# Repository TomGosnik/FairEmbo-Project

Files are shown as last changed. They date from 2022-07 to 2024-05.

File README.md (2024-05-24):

# FairEmbo - Fragmentation of surgical suture thread: 0.3, 0.5, 0.7, 0.9 mm

  ## Context
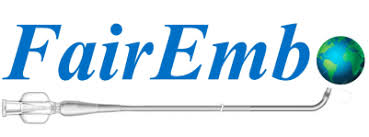
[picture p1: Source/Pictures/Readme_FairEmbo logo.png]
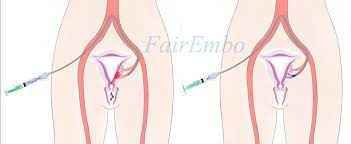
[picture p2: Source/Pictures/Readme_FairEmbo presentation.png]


This is part of a research project to previde a new solution to the problem of embolisation in low income countries. The [FAIREMBO chair](https://www.univ-amu.fr/en/public/fairembo-chair) from Marseille Hospital in France is a the origin of the innovation and we have here the plans of the machine that allows a mass cutting of particules necessary to achieve the operation.

Embolisation is a technology whose objective is to stop bleeding or blood circulation in a targeted area. The process seals a vessel by injecting a product into an artery under local anaesthetic. 

The embolisation procedure is not often used or considered in underdeveloped countries because embolisation equipment is simply not affordable in some countries. For one operation, several hundred euros are required, which is simply not possible in some cases. So there is an unaffordable demand for third world countries. In addition, the embolisation product is not well distributed in these countries, so additional costs would have to be incurred for importing the goods needed to carry out the procedure.
It is then necessary to find a solution to develop and provide embolisation procedures for underdeveloped countries. This solution must be affordable and easy to implement in these countries. 

In the search for an affordable solution to enable developing countries to access embolisation procedures, the Radiology and Medical Imaging Department of the Marseille Hospital (France) is proposing a new solution using suture particles injected in large quantities into the arteries to seal the vessels. 
In the case of the product used today, the embolisation is done chemically and increases the chance of thrombosis.
In the case of sutures, it is the mechanical effect of the accumulation of pieces of suture that allows the embolisation of the vessel. 

Our customer, contacted us to think about the creation of a machine to cut the suture before the medical intervention. The suture is given in spools and the prototype must provide the cut particles and answer different functions presented in the specifications of the machine.

The main objective of this project is to design and manufacture a device which is capable of taking input in the form of suture spools, and providing output in the form of cut sutures suitable for the FairEmbo process. The design should be simple, easy to use and, above all, cost-effective. In this way, the project will contribute to the automation of the Fairembo technique without losing sight of the main objective of affordability for poor underdeveloped countries.

This project has been initiated and developed in collaboration with the S-MART platform of Grenoble University (https://s-mart.grenoble-inp.fr/).

*For more information on the [FairEmbo project](https://www.youtube.com/watch?v=6P3fuX9SuC4)*

  ## Our product
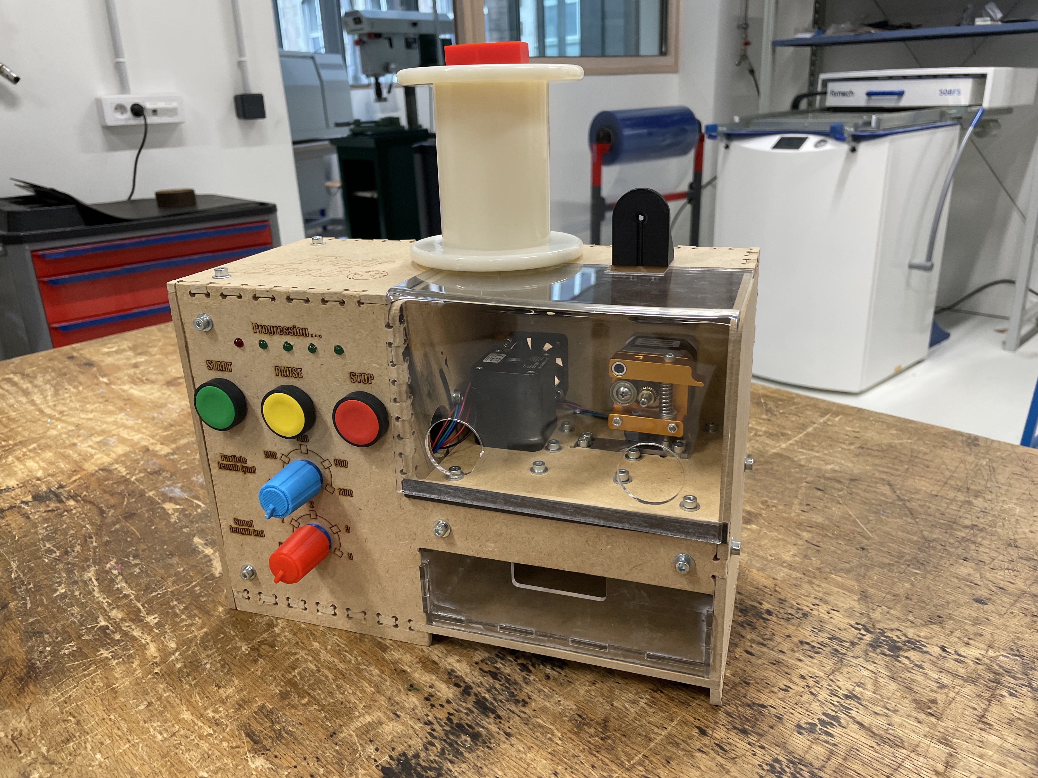
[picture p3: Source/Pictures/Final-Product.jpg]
  
  
  Photo of the particules as a result of the cutting operation: 0.3, 0.5, 0.7, 0.9 mm
    
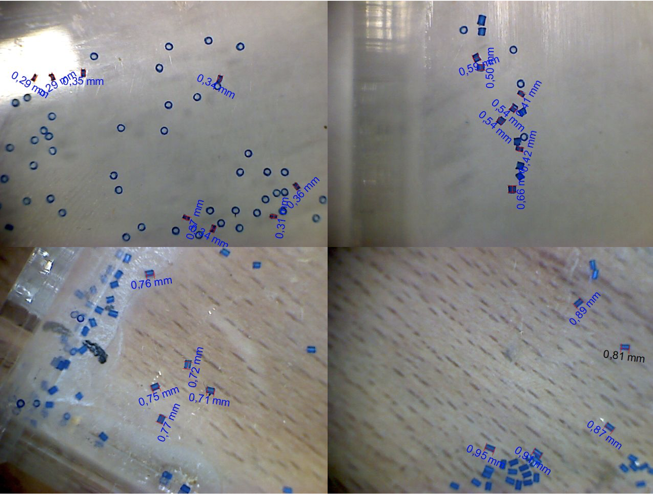
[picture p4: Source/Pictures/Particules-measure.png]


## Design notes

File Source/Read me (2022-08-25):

Insert Here a presentation of the content of the repository

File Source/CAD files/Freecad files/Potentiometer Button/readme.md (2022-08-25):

This component is downloaded from tracepart
# link of this component:
[Bouton de potentiomètre Sifam, axe de 6mm, Diamètre de 11mm, Enfichable](https://www.traceparts.com/fr/product/rs-components-bouton-de-potentiometre-sifam-axe-de-6mm-diametre-de-11mm-enfichable?CatalogPath=TRACEPARTS%3ATP10015001008002002&Product=10-23022015-110121&PartNumber=3%2F03%2FDR110-006%2F237%2F224)

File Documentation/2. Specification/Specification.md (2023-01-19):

# Specification
  
## 1. Stakeholders:
  
**Definition:** *Stakeholders generally refer to all the actors (human and non-human) who have an interest in a product. Among the stakeholders, there are both internal players, such as users and participants of the project, and external players that are represented by the potential user of products or external entities.*

<p align="center">
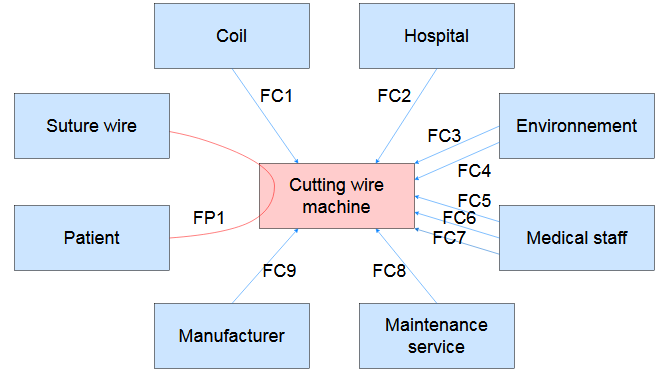
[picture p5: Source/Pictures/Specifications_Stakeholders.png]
  
<p/>

**FP1:** Cutting suture into particles

**FC1:** Be able to adapt to several types of suture bobbins

**FC2:** Be inexpensive

**FC3:** Be robust

**FC4:** Be able to adapt to its environment

**FC5:** Be lightweight and small in size

**FC6:** Be self-contained

**FC7:** Be easy to use

**FC8:** Be maintainable

**FC9:** Be reproducible
  
## 2. External interfaces
  
**Definition:**  *External interfaces are interactions between the product and the stakeholders.*

<p align="center">
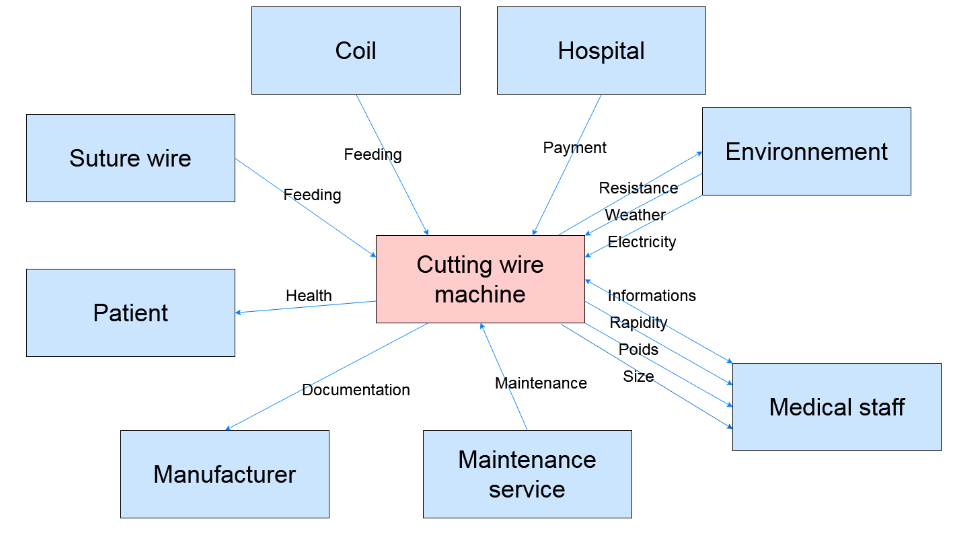
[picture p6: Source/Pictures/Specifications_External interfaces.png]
  
<p/>

## 3. Requirement

**Definition:** *A requirement is a formal statement that specifies when condition C is true, property P of object O is actual and its value shall belong  to domain D.*

* Cutting suture into particles
  * Particle size : between 300 and 1100 µm	(precision +/-75µm)
  * thread diameter : 0.3 to 0.5 extruded surgical suture thread
  * Particle shape : cylindrical (validated if the particles can exit the syringe)
  * Particle recovery
  * Speed of the process : less than 1s/particle

* Be able to adapt to several types of suture bobbins
  * Inner diameter 
  * Outside diameter
  * Wire length

* Be inexpensive
  * Cost : less than 500€ in parts

* Be robust
  * Drop resistance : functional after a drop of at least 1m
  * Lifetime 

* Be self-contained
  * Unattended operation time : Stops only when there is no more wire or when the user requests it (+/- 1s)

* Be easy to use
  * User documentation : can be used without instructions or training (possibility to integrate operating steps)
  * Accessibility of controls : can be used without the need for special dexterity
  * Quick to set up : less than 5 minutes

* Be maintainable
  * Demountability : access to components in the machine possible by hand or with a simple tool
  * Accessible materials, manufacturing techniques and components : use of materials, manufacturing techniques and components found in a conventional FabLab

* Be reproducible
  * Comprehensive documentation content : must be comprehensive and clear enough to be constructed by a third party
  * Accessibility of documentation : must be found on the internet
  * Accessible materials, manufacturing techniques and components : use of materials, manufacturing techniques and components found in a conventional FabLab

* Be lightweight and small in size
  * Mass : less than 3kg
  * Volume : between 3 and 10 dm3
 
* Be able to adapt to its environment
  * Power supply : 230V (+/- 1V)
  * Temperature : between 0 and 50 °C

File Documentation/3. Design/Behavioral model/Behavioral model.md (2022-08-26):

# Behavioral model

The system is composed of two mechanically moving parts. These two movements are driven by the two stepper motors: 
- the one linked to the extruder which guides and advances the wire,
- the one linked to the cam which cuts the wire.

## Wire guide

The first stepper motor is connected to an extruder, used today in 3D printers. An extruder is composed of different parts that are important for its operation:
- a gear wheel attached to the motor shaft,
- a ball bearing pressed against the gear wheel to prevent the wire from slipping,
- a nozzle that guides the wire to the place where it will be cut.

The gear wheel drives the bearing, which causes the wire to translate as shown below.
The translation and therefore the step corresponding to the size of the cut particles are therefore the image of the step imposed by the stepper motor.

<p align="center"> 
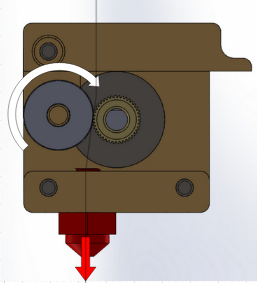
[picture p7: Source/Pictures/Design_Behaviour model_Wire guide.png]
 
</p>

## Wire cutting

The principle of cutting is that of the cam which transforms the rotational movement imposed by the motor into a translational movement.
A cam is an off-axis cylinder, i.e. the radius is not the same depending on the angle of rotation. It is this difference in radius that allows the red part to be translated (see below). 

To avoid friction, a ball bearing is used to link the cam and the red part.

This red part is guided in translation with a rail system. This red part is also directly screwed to the mobile blade, which is itself in translation against the second immobile blade.

In order to be able to move back and forth on the blade system, it was decided to use springs so that the red part could return to its initial position.

<p align="center"> 
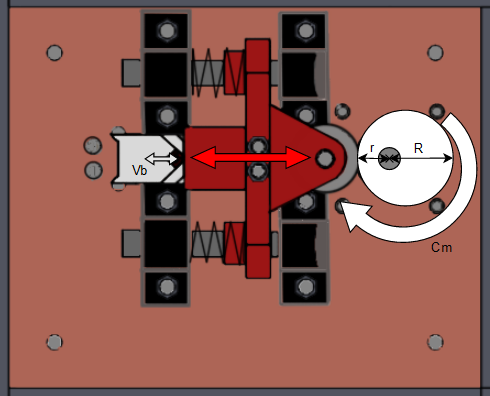
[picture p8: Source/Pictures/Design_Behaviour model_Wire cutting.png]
 
</p>

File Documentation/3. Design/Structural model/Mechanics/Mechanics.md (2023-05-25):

# How to document a structural model of mechanical products? 

 ## 1. Architectural structure

- **Definition:** *The architectural structure is a physical or logical layout of the components of a system design and their internal and external connections.*

 ### Architectural tree
 
<p align="center">
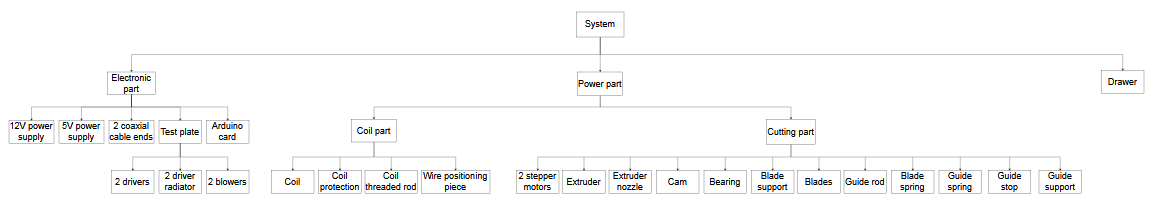
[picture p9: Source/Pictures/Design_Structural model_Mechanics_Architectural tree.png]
  
</p>
 
   ### Architectural graph

 - **Explanation:** The Template contains 2 main flow streams : 1. Power supply(represented in red), 2. Suture Wire (represented in green)

<p align="center">
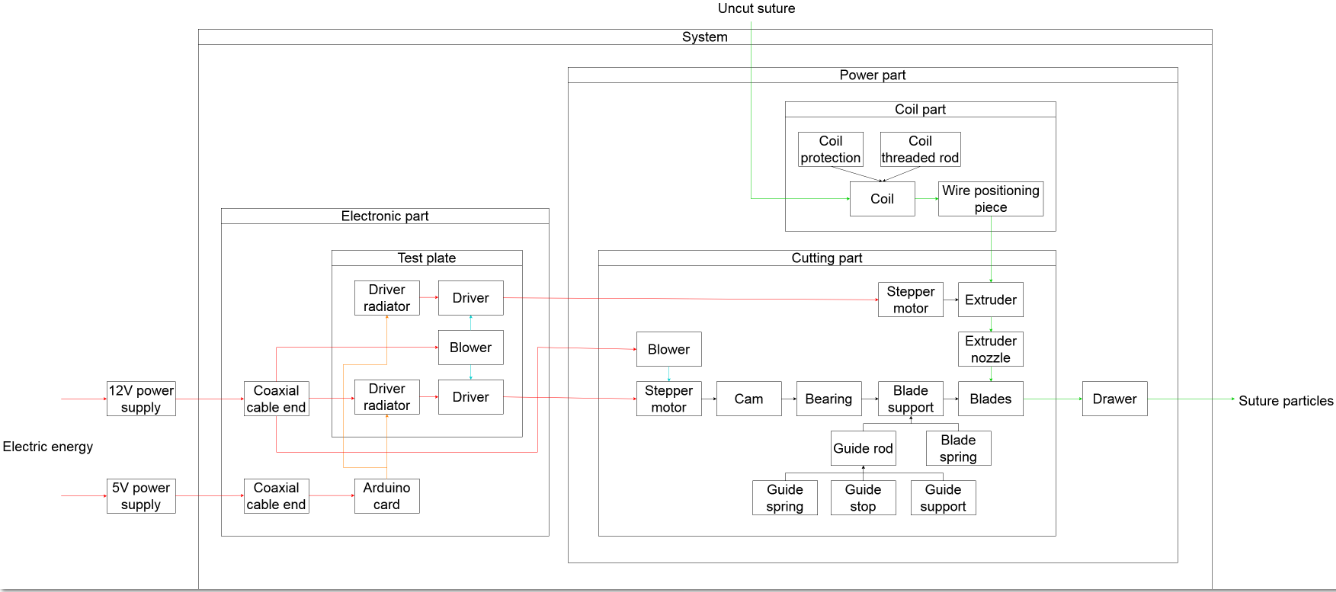
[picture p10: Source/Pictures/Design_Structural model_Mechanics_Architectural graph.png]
  
</p>

## 2. Editable CAD files
 *Fairembo was designed in SolidWorks (version 2021) and Freecad (version 0.19), allowing you to have full access to view, copy, edit, and export all of the source 3D CAD models for free from any computer which has installed Freecad and SolidWorks* 

  ### Template of file format

  1. 3D/2D file format
     * '.FCStd' is the original Freecad file format, allowing you to change the dimensions of the component as you want
     * '.STEP' is a neutral format which is for representative use such as Stepper Motor, Arduino card.
     * '.Dxf' is a 2D file format which allow you to use it in laser cutting
     * '.Stl' is a 3D file format which mostly used in 3D printing
  2. Name of CAD software

 Name of software | Version used | Download link 
|:---:|:---:|:---:|
SolidWorks | 2021 | https://www.solidworks.com/sw/support/downloads.htm 
FreeCAD| 0.19 | https://www.freecadweb.org/downloads.php
OnShape | 2021 |https://cad.onshape.com/documents/1c97d2eae284a43686a399bf/w/0fb098345c6d2285c3f1eb61/e/92be17f8a49da64bbd5fd24f
 
## 3. Characteristics of the materials
  
   ### Table of material Characteristics
 
 Name of material |	Density (g/cm3) |	Compressive Strength (MPa) |	Elastic Modulus (GPa) | Max Operating Temp (°C) | life span (years) | Price(european region) |	 Advantage |  Disadvantage |	link of reference 
|:---:|:---:|:---:|:---:|:---:|:---:|:---:|:---:|:---:|:---:|
Medium density fibreboard(MDF) | 0.75 | 10 | 4.0 | up to 130 | more than 10 | 7€ per m2 for thickness of 3mm | inexpensive, easy to recycle, solid, easy to manufacture (laser cutting, paint...) | heavy, absorb water faster than wood | [Medium Density Fiberboard](https://www.makeitfrom.com/material-properties/Medium-Density-Fiberboard-MDF/), [Physical and mechanical properties of MDF panels containing burned wood](https://www.researchgate.net/figure/Physical-and-mechanical-properties-of-MDF-panels-containing-burned-wood_tbl3_257485673), [Maximum core temperature (MCT) for MDF mats at various MCs](https://www.researchgate.net/figure/Maximum-core-temperature-MCT-for-MDF-mats-at-various-MCs_fig4_237372503), [Advantages & Disadvantages of MDF - Fiber Board](https://civiltoday.com/civil-engineering-materials/timber/163-advantages-and-disadvantages-of-mdf), [Price for MDF in France](https://www.smbois.com/panneaux-bois/panneaux-mdf/mdf.html)
Plexiglass (PMMA) | 1.18 | 75,84 to 131 | - | 65 to 93 | 30 and even more | 25€ to 140€ per m2 for thickness from 1mm to 15mm | inexpensive, easy to manufacture (laser cutting, folding...), light | not resistant to heat | [Technical Data Sheet Plexiglass (PMMA)](https://laminatedplastics.com/plexiglass.pdf), [PLEXIGLAS®: A VALUABLE MATERIAL EVEN AFTER USE](https://www.plexiglas.de/en/sustainability/easy-to-recycle), [Acrylic advantages and disadvantages](https://plasticsheetsshop.co.uk/acrylic-advantages-and-disadvantages/#:~:text=Advantage%3A%20Plexiglass%20is%20hardwearing%20Acrylic%20sheet%20is%20very,same%20levels%20of%20thermal%20efficiency%20as%20standard%20glass), [plexiglas shop](https://www.plexiglas-shop.com/)
Aluminum | 2.6898 | - | 68.3 | - | 40 to 80 | 2.1€ to 3.5€ per Kg | lighter than other metal, easy to manufacture( lathe, milling..) | - | [Aluminium: Specifications, Properties, Classifications and Classes](https://www.azom.com/article.aspx?ArticleID=2863), [THE LIFESPAN AND RECYCLABILITY OF ALUMINIUM AND STAINLESS STEEL](https://www.metalswarehouse.co.uk/lifespan-recyclability-aluminium-steel/), [Aluminium Price Today](https://markets.businessinsider.com/commodities/aluminum-price/euro#:~:text=1%20Ton%20%3D%201%2C000%20Kilograms.%20%0AAluminium%20Price%20,%20%20%20Per%201%20Kilogram.%202.34%20EUR).
Acrylonitrile butadiene styrene (ABS) | 0.9 to 1.53 | 65 | 2.28 | −20 to 80 | 50 to 80 | 25$ per Kg | resistant to physical impact, easy to use for 3D print | inappropriate for high-temperature condition, high smoke generation when it burns| [ABS's properties from wiki](https://en.wikipedia.org/wiki/Acrylonitrile_butadiene_styrene), [Typical Compressive Yield Strength and Compressive Modulus of Polymers](https://matweb.com/reference/compressivestrength.aspx), [What is the average life expectancy of ABS pipe?](https://www.howtolookatahouse.com/Blog/Entries/2018/7/what-is-the-average-life-expectancy-of-abs-pipe-1.html#:~:text=The%20expected%20lifespan%20of%20ABS%20%28Acrylonitrile%20Butadiene%20Styrene%29,is%20expected%20to%20be%20similar%20to%20PVC%20pipe), [ABS plastic properties](https://adrecoplastics.co.uk/abs-plastic-properties/#:~:text=ABS%20has%20a%20low%20melting%20point%2C%20which%20enables,to%20withstand%20heavy%20use%20and%20adverse%20environmental%20conditions), [How Much Does 3D Printing Filament Cost](https://3dinsider.com/3d-printing-filament-cost/#:~:text=Regular%20PLA%20and%20ABS%20filament%20for%203D%20printing,amount.%20Not%20all%203D%20printing%20materials%20are%20equal).

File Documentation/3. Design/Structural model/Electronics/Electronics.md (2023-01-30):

# Structural model: Electronics

## 1. Nomenclature

The list of components with references and examples of links to usable sites:

Component name	| Nomenclature |	number of components |	Characteristics |	Links to the sites |	Unit price (€)|
| :---: | :---: | :---: | :---: | :---: | :---: |
Stepper motor 1 (M1) |	PUISS_Mot_Extr |	1	| Moteur pas à pas Joy-it SM42HT38-1684A NEMA-17-01 0.4 Nm 1.68 A Diamètre de l'arbre: 5 mm 1 pc(s) |	https://www.conrad.fr/p/moteur-pas-a-pas-joy-it-nema-17-01-04-nm-168-a-diametre-de-larbre-5-mm-1-pcs-1597325	| 31,99 |
Stepper motor 2 (M2) |	PUISS_Mot_Cam |	1	| Joy-it Moteur pas à pas NEMA17-06 0.59 Nm 2 A 2 A Diamètre de l'arbre: 5 mm |	https://www.conrad.fr/p/joy-it-moteur-pas-a-pas-nema17-06-059-nm-2-a-2-a-diametre-de-larbre-5-mm-2355876	| 21,49 |
Driver 1 (D1)	| ELEC_Driv_Extr |	2	| TB6612FNG Dual Motor Driver Carrier	| https://www.pololu.com/product/713	| 9,95 |  
Driver 2 (D2)	| ELEC_Driv_Cam	|
Driver 1 radiator	| ELEC_Rad_Driv_Extr	| 2	 | Résistance thermique:123°C/W; Boîtiers refroidis:SOIC-8, SOIC-14, SSOP-16, TSSOP-14, TSSOP-16; Largeur externe - Métrique:6.3mm; Hauteur externe - Métrique:4.8mm; Longueur externe - 	| https://fr.farnell.com/webapp/wcs/stores/servlet /CompareProductsDisplay?catalogId=15001&langId=-2&storeId=10160&catentryId=64708491&pageType=PDP	| 0,618 | 
Driver 2 radiator	| ELEC_Rad_Driv_Cam | 				
Capacitor (C)	| ELEC_Cond	| 1	| Capacitor 47μF, 16V c.c.	| https://fr.rs-online.com/web/p/condensateurs-electrolytiques/7110927?cm_mmc=FR-PLA-DS3A-_-google-_-CSS_FR_FR_Passifs_Whoop-_-(FR:Whoop!)+Condensateurs+%C3%A9lectrolytiques-_-7110927&matchtype=&pla-339621668050&gclid=Cj0KCQjwxIOXBhCrARIsAL1QFCaT7Q_rE7X_4SQt8N8Zu6aHp6PKWwv3yTqLVZFDtoSgLZNFndHlv44aApaUEALw_wcB&gclsrc=aw.ds	| 0,078 | 
Pushbutton 1 (B1)	| ELEC_Bout_V	| 3	| Bouton-poussoir, NO, Montage panneau	| https://fr.rs-online.com/web/p/boutons-poussoirs/8151834?aud-871567053779%3Apla-365975203081&cm_mmc=FR-PLA-DS3A-_-google-_-CFS_FR_FR_Schneider_Whoop-_-(FR%3AWhoop!)%20Interrupteurs%20(2)-_-8151834&gclid=Cj0KCQjwxIOXBhCrARIsAL1QFCZbOdo6Ri0mEeT1leJcbMdhEjlsmj2F4bzqcQj8dS_wv5ovp86AldUaAt9hEALw_wcB&gclsrc=aw.ds&matchtype=	| 16,9 | 
Pushbutton 2 (B2)	| ELEC_Bout_J	|  
Pushbutton 3 (B3)	| ELEC_Bout_R	|  
Potentiometer 1 (P1)	| ELEC_Pot_H	| 2	| Potentiometer: Resistance 10kohm, 1 turn, Linear, 500mW, resistance tolerance ± 20%	| https://fr.farnell.com/tt-electronics-bi-technologies/p231-fc20br10k/potentiometre-rotatif-10k-20mm/dp/2771755?st=potentiometre%20rotatif	| 1,68 | 
Potentiometer 2 (P2)	| ELEC_Pot_B	| 			
Green LED 1 (L1)	| ELEC_LED_1	| 4	| LED Vert, Traversant, 5 mm (T-1 3/4), 2 V	| https://fr.rs-online.com/web/p/leds/7088022p?cm_mmc=FR-PLA-DS3A-_-google-_-CSS_FR_FR_Afficheurs_et_optoelectronique_Whoop-_-(FR:Whoop!)+LEDs-_-7088022P&matchtype=&pla-834413916684&gclid=Cj0KCQjwxIOXBhCrARIsAL1QFCYk1e3LMUt7p1XBNJRN2BUuUm2WMwk3iOHTFCnizzsr4hlkoqhmzT8aAi9eEALw_wcB&gclsrc=aw.ds	| 0,268 | 
Green LED 2 (L2)	| ELEC_LED_2	| 	
Green LED 3 (L3)	| ELEC_LED_3	| 		
Green LED 4 (L4)	| ELEC_LED_4	| 			
Red LED 5 (L5)	| ELEC_LED_5	| 1	| LED Rouge, Traversant, 5 mm (T-1 3/4), 2,6 V	| https://fr.rs-online.com/web/p/leds/1278393?cm_mmc=FR-PLA-DS3A-_-google-_-CSS_FR_FR_Afficheurs_et_optoelectronique_Whoop-_-(FR:Whoop!)+LEDs-_-1278393&matchtype=&pla-302722872933&gclid=Cj0KCQjwxIOXBhCrARIsAL1QFCYVfGLEzypoiNEvZWrra4NUpec1AlHI-cAAueNsmEW-s_PTFDmVd0UaAoqTEALw_wcB&gclsrc=aw.ds	| 0,088 | 
Resistance 1 (R1)	| ELEC_Resist_Bout_V	| 8	| Résistance Film carbone 100Ω ±5%, 0.25W	| https://fr.rs-online.com/web/p/resistances-traversantes/7077587	| 0,278 | 
Resistance 2 (R2)	| ELEC_Resist_Bout_J | 		
Resistance 3 (R3)	| ELEC_Resist_Bout_R | 			
Resistance 4 (R4)	| ELEC_Resist_LED_1	| 		
Resistance 5 (R5)	| ELEC_Resist_LED_2	| 			
Resistance 6 (R6)	| ELEC_Resist_LED_3	| 		
Resistance 7 (R7)	| ELEC_Resist_LED_4	| 			
Resistance 8 (R8)	| ELEC_Resist_LED_5	| 
5V power supply	| ELEC_Alim5V	| 1	| Alimentation AC/DC, ITE, 1 sortie, 2.75 W, 5 V, 550 mA	| https://fr.farnell.com/brainboxes/pw-600/power-supply-5v-1a-es-357/dp/2096366?st=alimentation%205v	| 27,77 | 
12V power supply	| ELEC_Alim12V	| 1	| Adaptateur AC/DC 12V c.c., 2A, 24W, , Régulée	| https://fr.rs-online.com/web/p/adaptateurs-ac-dc/1753324?cm_mmc=FR-PLA-DS3A-_-google-_-CSS_FR_FR_Alimentations_et_transformateurs_Whoop-_-(FR:Whoop!)+Adaptateurs+AC/DC-_-1753324&matchtype=&pla-370976687757&gclid=Cj0KCQjwxIOXBhCrARIsAL1QFCbjgBdOY3BMhupPiywYVdsT5aeT05L4zefR6RXDtFUW6gS1CuGbczEaAmj8EALw_wcB&gclsrc=aw.ds	| 16,26 | 
5V coaxial cable end	| ELEC_Embout_5V	| 2	| Prise d'alimentation CC, 5A, Montage sur CI, 12 V c.c.	| https://fr.rs-online.com/web/p/connecteurs-d-alimentation-dc/8051696	| 2,359 | 
12V coaxial cable end	| ELEC_Embout_12V	| 		
Ventilator 1	| ELEC_Ventilo_Mot	| 2	| Ventilateur axial RS PRO 5 V c.c., 11.9m³/h, 40 x 40 x 10mm, 1.92W	| https://fr.rs-online.com/web/p/ventilateurs-axiaux/7897858?cm_mmc=FR-PLA-DS3A-_-google-_-CSS_FR_FR_Chauffage_%26_ventilation_et_air_conditionne_Whoop-_-(FR:Whoop!)+Ventilateurs+axiaux+(2)-_-7897858&matchtype=&pla-475514636566&gclid=Cj0KCQjwxIOXBhCrARIsAL1QFCZHMrid9mmDNu3gS1Z1DK1VgvmU1g3jfntRcnVzLYc1X8ZK7yz8A9QaAoOXEALw_wcB&gclsrc=aw.ds	| 7,08 | 
Ventilator 2	| ELEC_Ventilo_Driv	| 		
Arduino card	| ELEC_Ard	| 1	| UNO Rév. 3 Arduino	| https://fr.rs-online.com/web/p/arduino/7154081?cm_mmc=FR-PLA-DS3A-_-google-_-CSS_FR_FR_Raspberry_Pi_%26_Arduino_%26_Outils_de_developpement_Whoop-_-(FR:Whoop!)+Arduino-_-7154081&matchtype=&aud-827186183686:pla-339391921421&gclid=Cj0KCQjwxIOXBhCrARIsAL1QFCZg_iLNqiF-tBPj6V5rdmA0EW2CjRNORrWGV6KyqY_00fqD72AHXBQaArdnEALw_wcB&gclsrc=aw.ds	| 28,1 | 
| | | | | Total	| 223,146 | 

Here is the composition tree of the electronic part of the device

<p align="center">
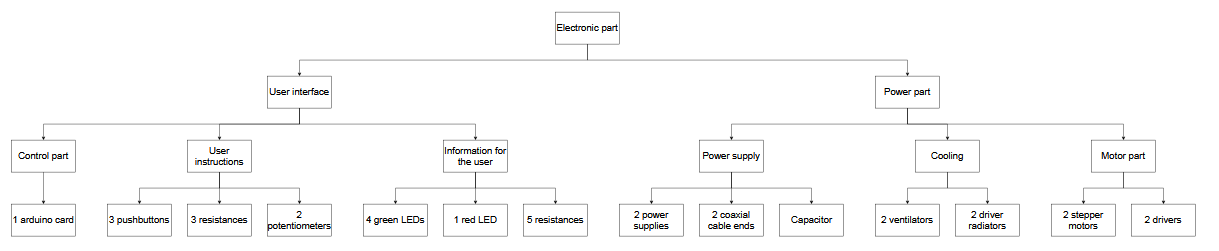
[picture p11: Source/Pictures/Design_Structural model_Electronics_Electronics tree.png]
  
</p>

## 2. Architectural structure

**Definition:** *The architectural structure is a physical or logical layout of the components of a system design and their internal and external connections.*

**Final version**
<p align="center">
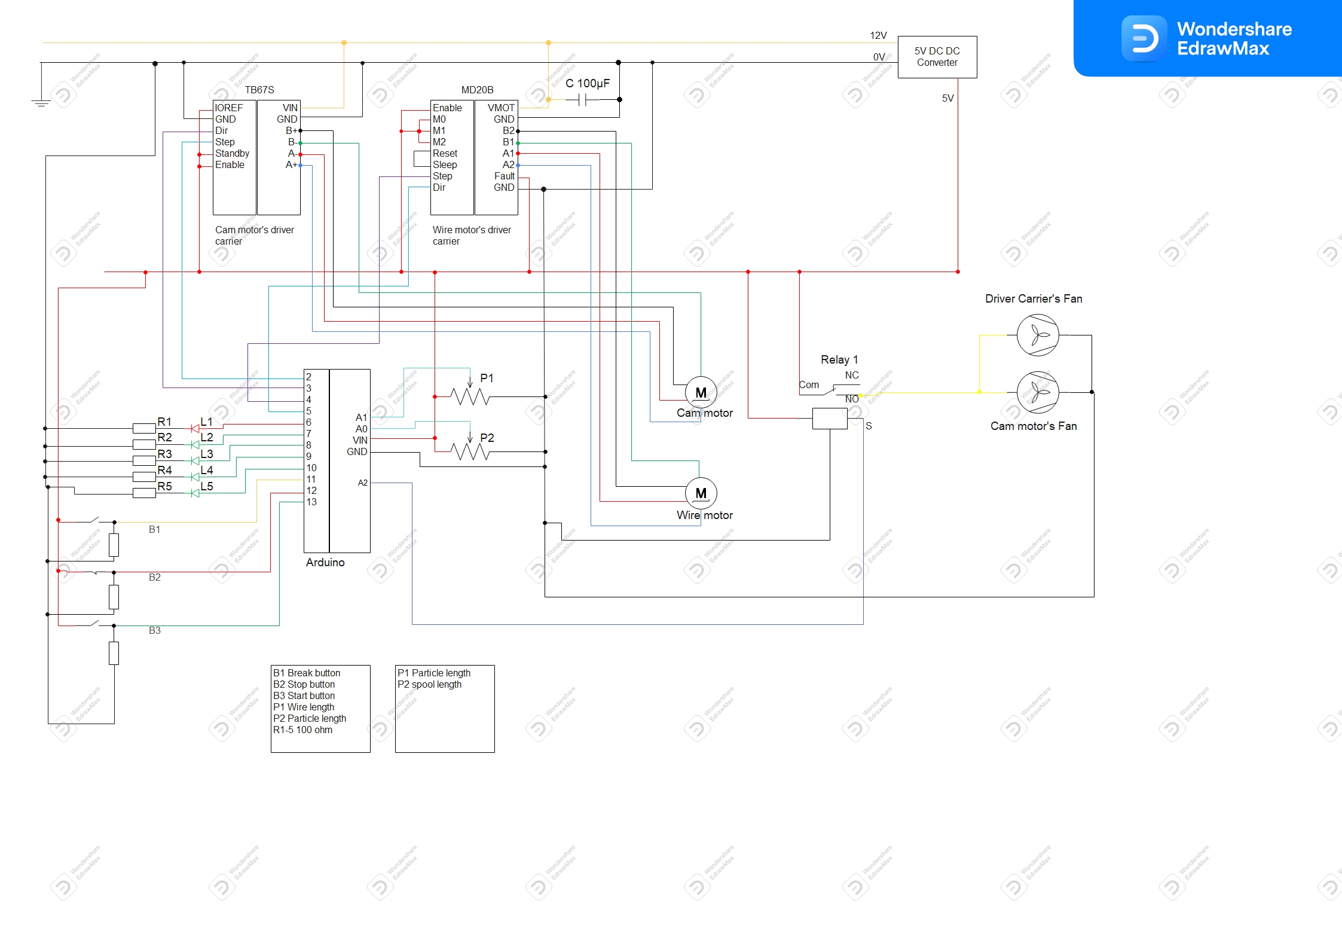
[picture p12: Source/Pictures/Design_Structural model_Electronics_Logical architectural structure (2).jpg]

</p>

Pinout diagram

<p align="center">
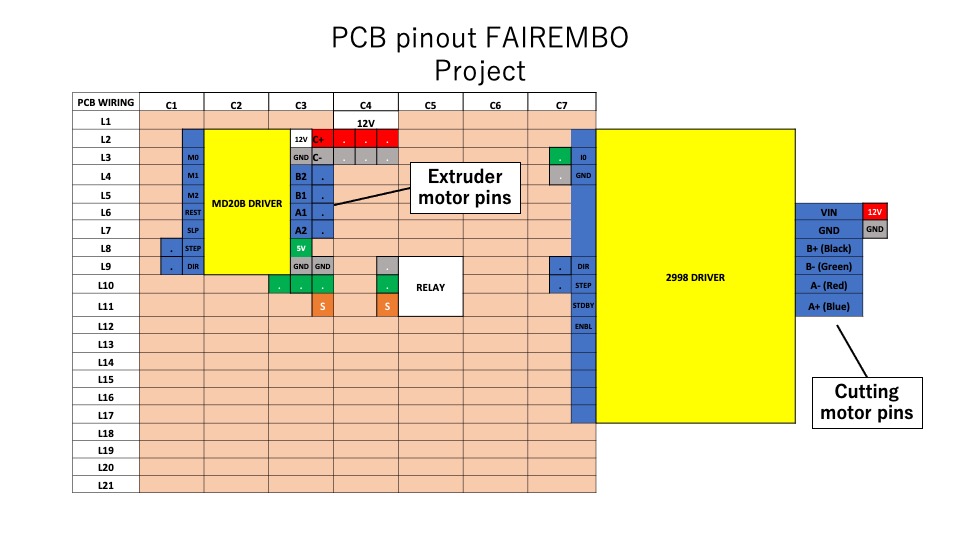
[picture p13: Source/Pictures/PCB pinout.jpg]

</p>

Driver control board - pinout correspondance

<p align="center">
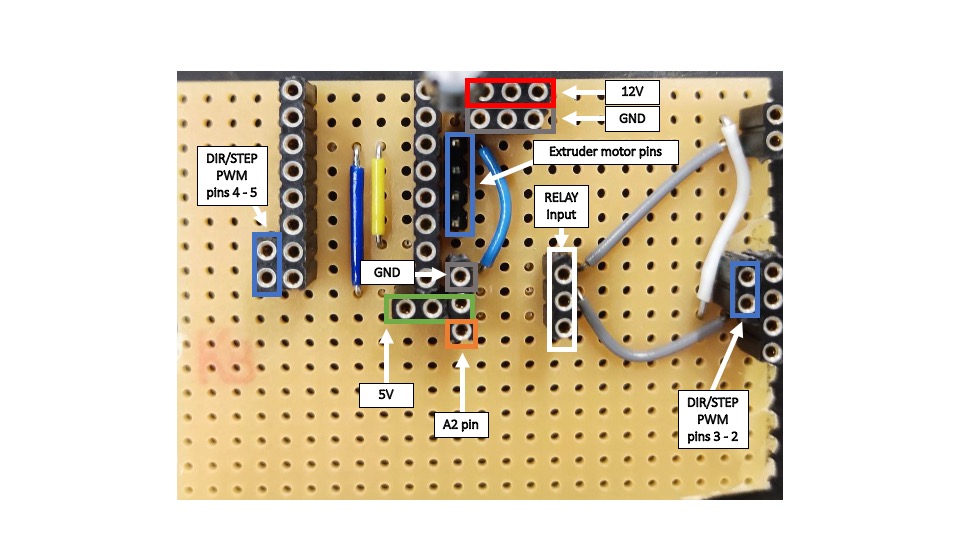
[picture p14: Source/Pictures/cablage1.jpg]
  
</p>

Picture of the card with relay and drivers mounted on 

<p align="center">
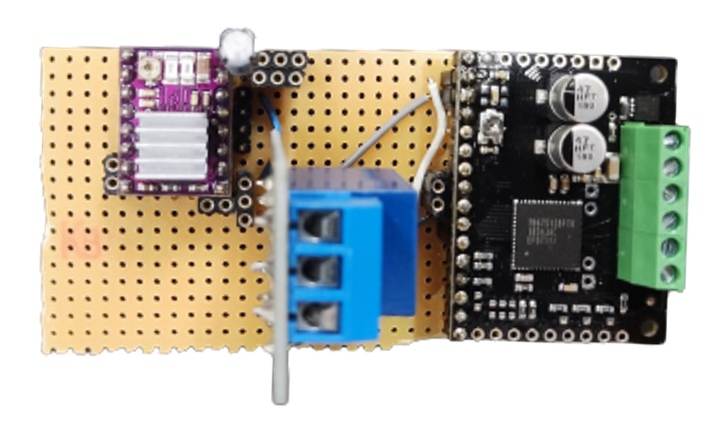
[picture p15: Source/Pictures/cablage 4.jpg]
  
</p>

Power wiring : (Note that ascending order of motor pin colors is always Blue - Red - Green - Black)

<p align="center">
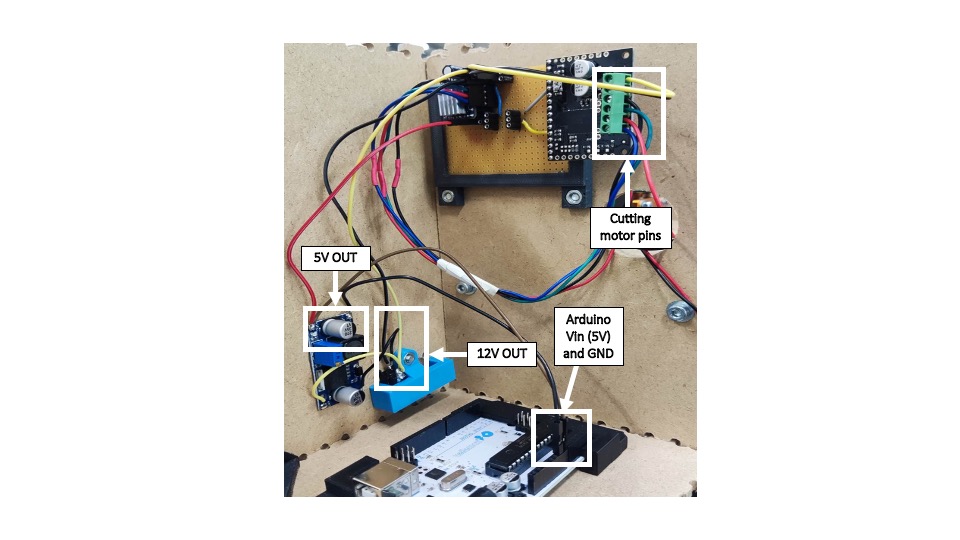
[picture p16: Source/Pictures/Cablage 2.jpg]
  
</p>

Front control panel: Potentiometers and control buttons arduino pin correspondance

<p align="center"> 
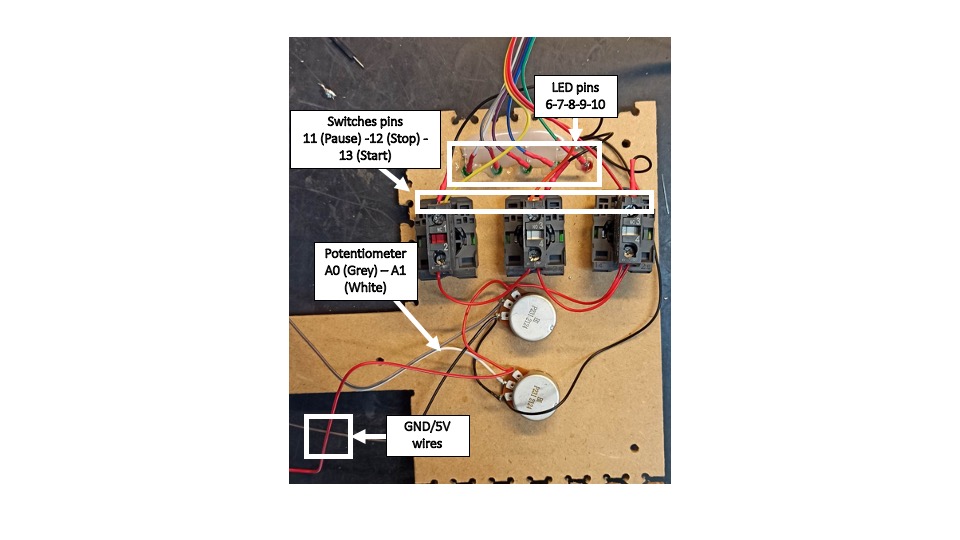
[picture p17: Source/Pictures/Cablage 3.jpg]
  
</p>

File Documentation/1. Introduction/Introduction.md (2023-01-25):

# Introduction

## Motivations

The motivation for the project is to make access to embolisation possible in the most disadvantaged countries.
With the use of suture particles replacing the technology used today, this is now possible.

However, the cutting process must be precise, in large quantities and with an ajustable particles' length. Because it must meet the needs of different patients.
Manual scissor cutting is therefore not sufficient, so it is necessary to automate the process. 

## Goals

The aim of the project is to produce a machine that meets these requirements. 

This machine must be usable and adapted for regular use in a hospital. 
The interface must therefore be accessible for all staffs with simple but detailed instructions.
In addition, the cut thread can be found from a standard suture spool.

## History

The project originated from a group of health professionals, chaired by Professor Vincent Vidal.
Mr. Mathieu DE BIGLIESCE is the doctor who contacted us so that we could launch the project

## Documentation structure

- Introduction
- Specification
- Design 
- Manufacturing
- Assembly
- Use
- Maintenance
- Disposal

## Required skills

To reproduce or modify the cutting machine, it is necessary to know the basic mechanics as well as the electronics and coding related to the Arduino. This product has been intentionnally designed to be manufactured in any fablab with cutting machines and 3D printers.

## Contribution Process

The machine has been delivered to the Marseille Hospital and is currently under test in various hospitals. An improved version will certainly be welcome in a near future. We will search for input and participation soon. In any case you can contact: jean-francois.boujut@grenoble-inp.fr

## Last updates 

January 2023

## Initial project team

| Tom GOSNIK | Chaoji LIANG | Tom BIANCIOTTO | Adrien BACCONNET
| :---: |
| Students at Grenoble INP - School of Industrial Engineering and Management | and University Grenoble Alpes (UGA) - Phitem |
| tom.gnk@gmail.com | liangchaoji04@gmail.com |

## License
Attribution - Share Like
CC BY-SA

This license lets others remix, adapt, and build upon your work even for commercial purposes, as long as they credit you and license their new creations under the identical terms. This license is often compared to “copyleft” free and open source software licenses. All new works based on yours will carry the same license, so any derivatives will also allow commercial use. This is the license used by Wikipedia, and is recommended for materials that would benefit from incorporating content from Wikipedia and similarly licensed projects.

<br />Ce(tte) œuvre est mise à disposition selon les termes de la <a rel="license" href="http://creativecommons.org/licenses/by-sa/4.0/">Licence Creative Commons Attribution -  Partage dans les Mêmes Conditions 4.0 International</a>.

## Sponsors and Partners

https://genie-industriel.grenoble-inp.fr/

https://s-mart.fr/

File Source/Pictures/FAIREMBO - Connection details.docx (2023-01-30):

FAIREMBO - Connection details

Pinout diagram :

Correspondences on the real card - relative pins on arduino :

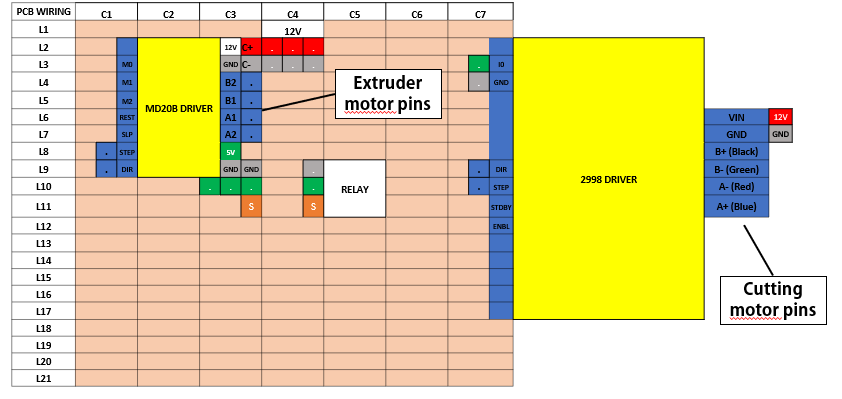
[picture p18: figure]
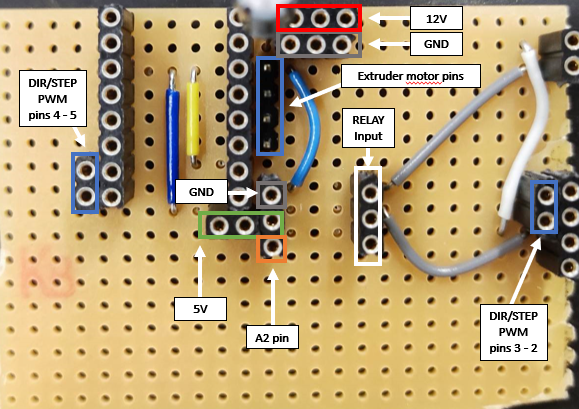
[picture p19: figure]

Picture of the card with relay and drivers mounted on :

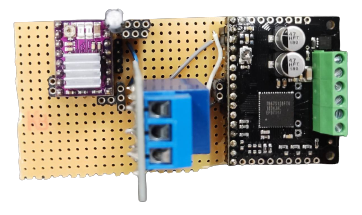
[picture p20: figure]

Power wiring : (Note that ascending order of motor pin colors is always Blue - Red - Green - Black)

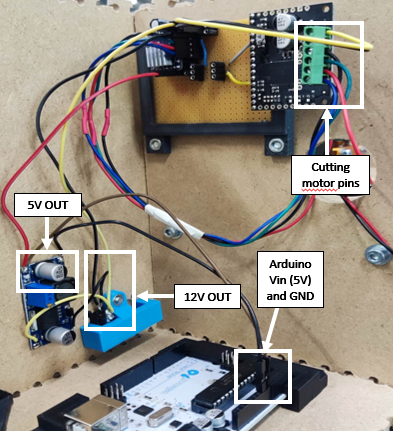
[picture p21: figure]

Front panel details (and relative pins for arduino) :

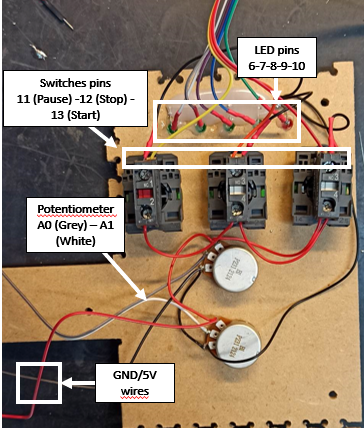
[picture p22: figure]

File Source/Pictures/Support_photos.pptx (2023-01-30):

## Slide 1

PCB pinout FAIREMBO Project

PCB WIRING | C1 | | | C2 | | | C3 | | | C4 | | | C5 | C6 | C7
L1 | | | | | | | | | | 12V
L2 | | | | MD20B DRIVER | | | | 12V | C+ | . | . | . | | | | | | 2998 DRIVER
L3 | | | M0 | | | | | GND | C- | . | . | . | | | | . | I0
L4 | | | M1 | | | | | B2 | . | | | | | | | . | GND
L5 | | | M2 | | | | | B1 | .
L6 | | | REST | | | | | A1 | . | | | | | | | | | | | | VIN | 12V
L7 | | | SLP | | | | | A2 | . | | | | | | | | | | | | GND | GND
L8 | | . | STEP | | | | | 5V | | | | | | | | | | | | | B+ (Black)
L9 | | . | DIR | | | | | GND | GND | | | . | RELAY | | | . | DIR | | | | B- (Green)
L10 | | | | | | | . | . | . | | | . | | | | . | STEP | | | | A- (Red)
L11 | | | | | | | | | S | | | S | | | | | STDBY | | | | A+ (Blue)
L12 | | | | | | | | | | | | | | | | | ENBL
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
Extruder motor pins

Cutting motor pins

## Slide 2

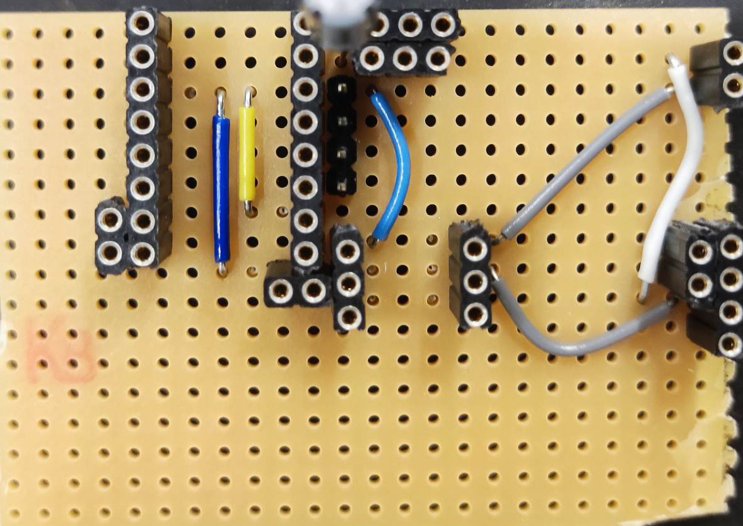
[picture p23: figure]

12V

GND

DIR/STEP
PWM pins 4 - 5

Extruder motor pins

RELAY Input

GND

5V

DIR/STEP
PWM pins 3 - 2

A2 pin

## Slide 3

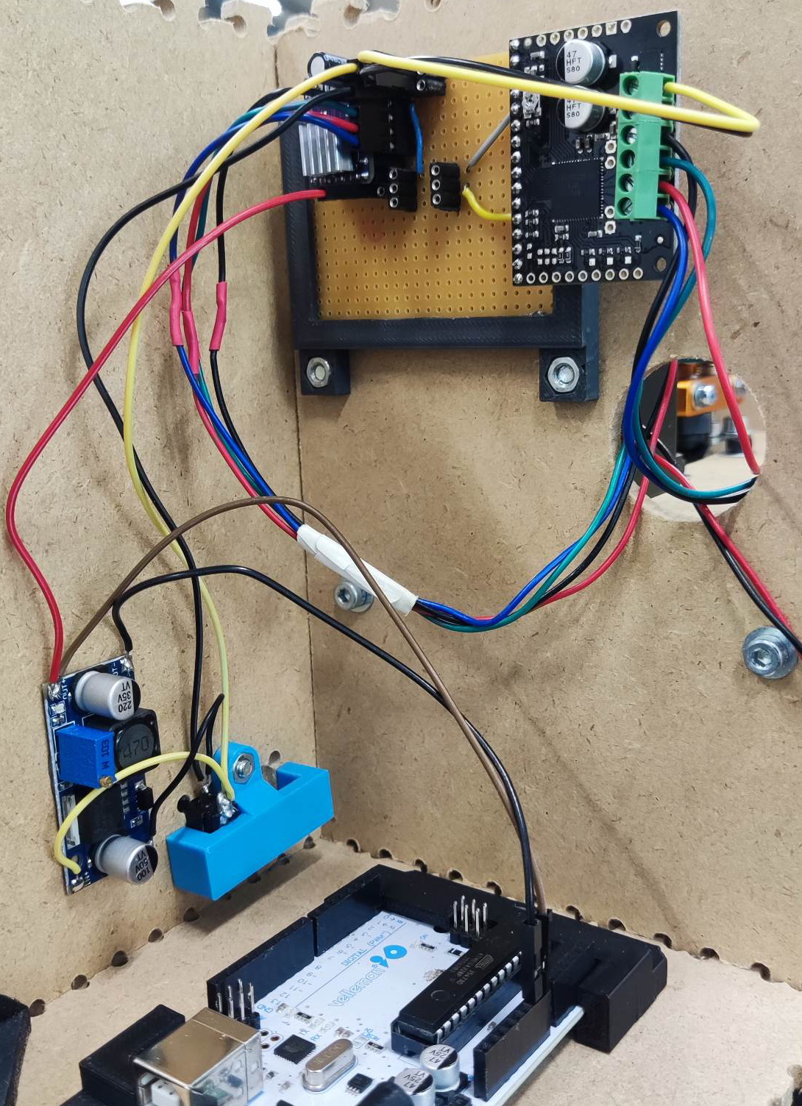
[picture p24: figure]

Cutting motor pins

5V OUT

Arduino Vin (5V) and GND

12V OUT

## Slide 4

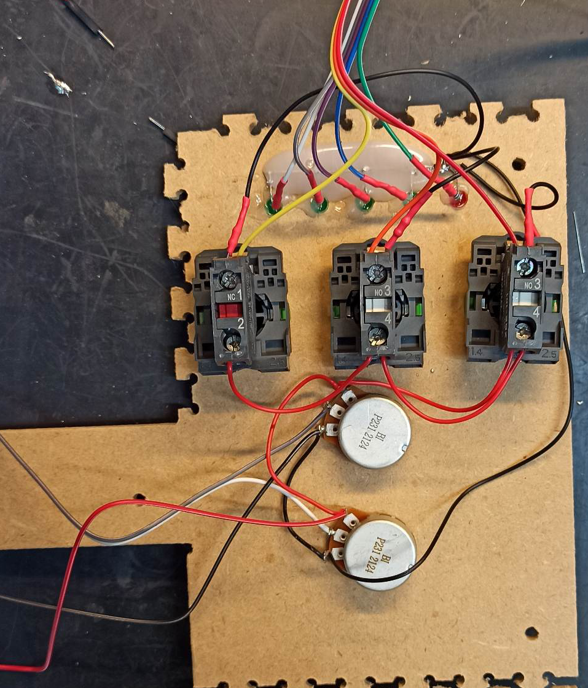
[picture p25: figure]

LED pins
6-7-8-9-10

Switches pins
11 (Pause) -12 (Stop) -13 (Start)

Potentiometer
A0 (Grey) – A1 (White)

GND/5V wires

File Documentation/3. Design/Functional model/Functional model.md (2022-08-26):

# Functional model

## 1. Functional tree
 
- **Definition:** *The functional tree is a top-down decomposition of function into sub-functions that helps to simplify the problem to solve.*

<p align="center"> 
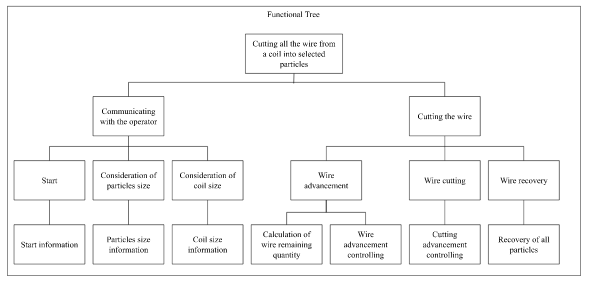
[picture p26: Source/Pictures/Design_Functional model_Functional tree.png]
 
</p>

## 2. Functional graph

- **Definition:** *The functional graph is a multi-level logical articulation of technical functions.*

<p align="center"> 
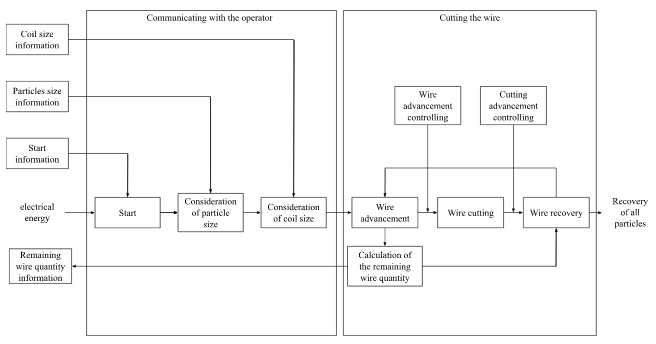
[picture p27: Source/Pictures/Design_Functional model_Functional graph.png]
 
</p>

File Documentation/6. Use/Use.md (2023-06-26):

# **Use**

*I would like to provide important information to end-users on 'how to use the FAIREMBO Machine'.*

## **User videos**
[Video presentation of the machine (in French)](https://youtu.be/ImHSvuk8Stc)

[Video presentation of the insetion of the thread (in French)](https://youtu.be/wi5pOOeNl6A)

## **User guide**
*The user guide can help the maker to understand how to use a product.* 

<p align="center"> 
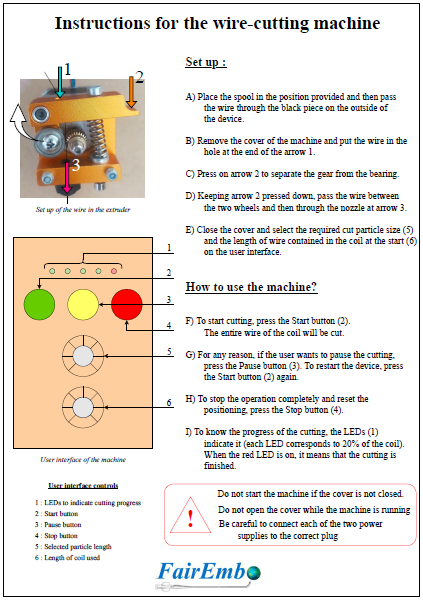
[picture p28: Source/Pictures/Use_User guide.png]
 
</p>

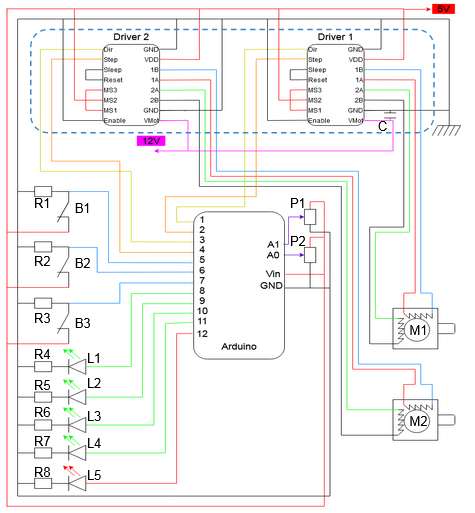
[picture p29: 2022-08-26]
Source/Pictures/Design_Structural model_Electronics_Logical architectural structure.png

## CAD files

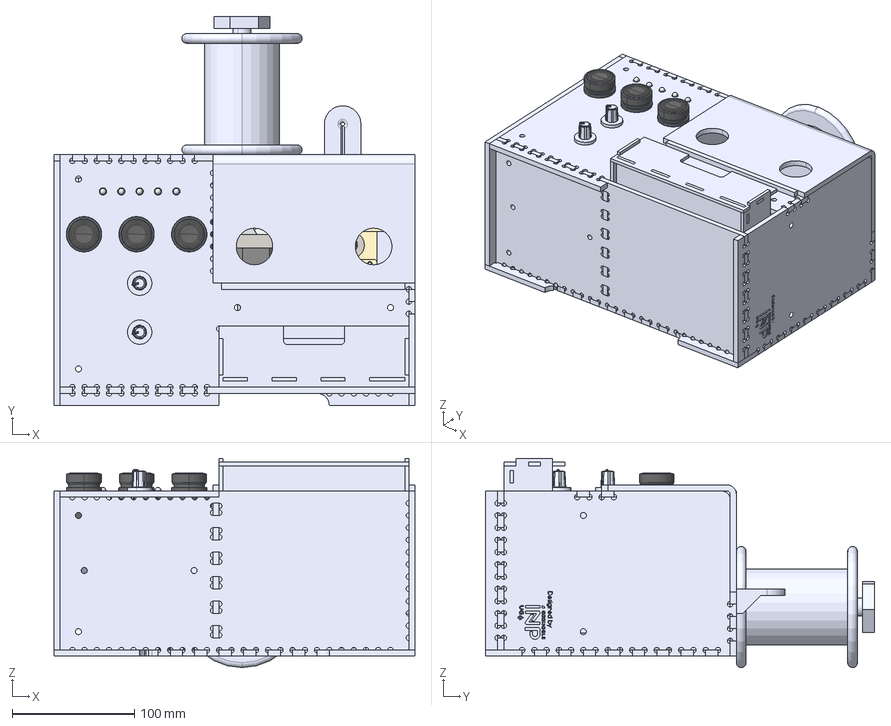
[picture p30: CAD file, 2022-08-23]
Source/CAD files/Full assembly without fastener/Full Assembly.FCStd
295.0 x 318.0 x 170.9 mm
STRUCT_Pl_B
STRUCT_Pl_AR
STRUCT_Pl_AV
STRUCT_Pl_G
STRUCT_Pl_M
STRUCT_Pl_H
STRUCT_Pl_D
STRUCT_Couv
ELEC_Bout_V
ELEC_Bout_J
ELEC_Bout_R
STRUCT_Pl_P-Aim_H
STRUCT_Pl_P-Aim_AV
STRUCT_Bob_TF
STRUCT_Pl_Puiss
PUISS_Guid_But_AR
PUISS_Guid_Sup_AR
PUISS_Guid_But_AV
PUISS_Guid_Sup_AV
PUISS_L_Immob
PUISS_Guid_Tige_AR
PUISS_Guid_Tige_AV
STRUCT_Eq_Puiss_D_AR
STRUCT_Eq_Puiss_G_AR
STRUCT_Eq_Puiss_G_AV
STRUCT_Eq_Puiss_D_AV
STRUCT_Eq_Interf_B_AV
STRUCT_Eq_Interf_B_AR
STRUCT_Eq_Interf_H_AV
STRUCT_Eq_Interf_H_AR
PUISS_L_Mob
Part 4.step
Part 1.step
Part 2.step
Part 3.step
PUISS_Cam
Part 4.step001
Part 1.step001
Part 2.step001
Part 3.step001
PUISS_Buse
Puiss_RaB_Extr
PUISS_Extr_R
PUISS_Extr_R001
PUISS_Extr_R002
PUISS_L_P-L
PUISS_Guid_RaB
STRUCT_T_B
STRUCT_T_AV
STRUCT_T_G
STRUCT_T_AR
STRUCT_T_D
ELEC_Ard
ELEC_P-Ard_D
ELEC_P-Ard_G
Assembly of driver
ELEC_P-Driv
ELEC_LED_5
ELEC_LED_4
ELEC_LED_3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

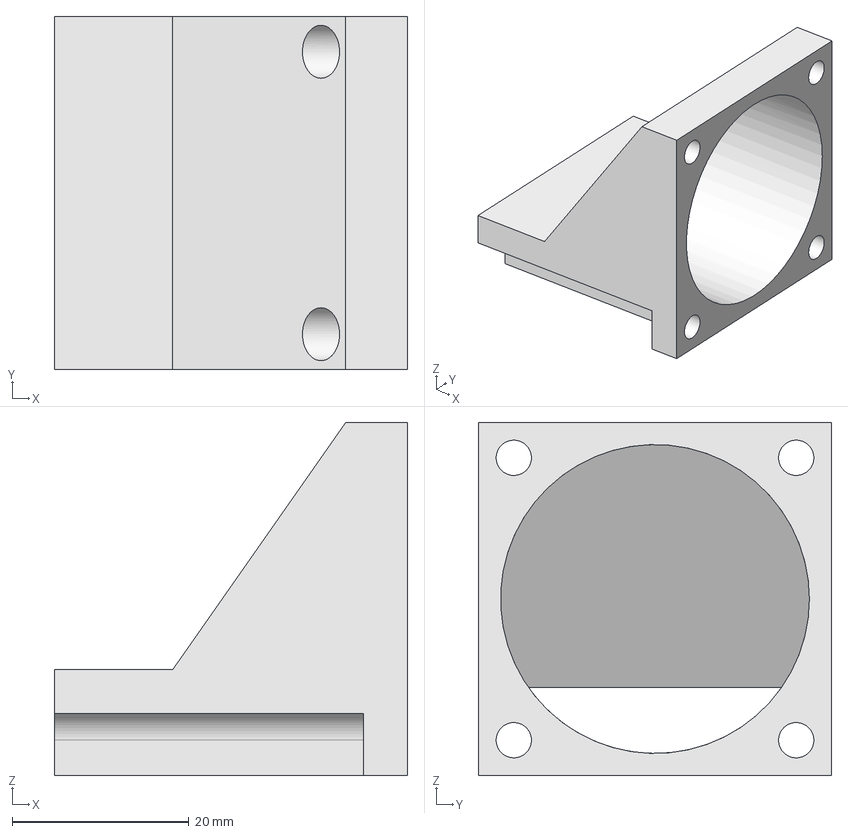
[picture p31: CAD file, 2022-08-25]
Source/CAD files/Freecad files/Air diverter for drivers/ELEC_Dir-air.FCStd
40.0 x 40.0 x 40.0 mm

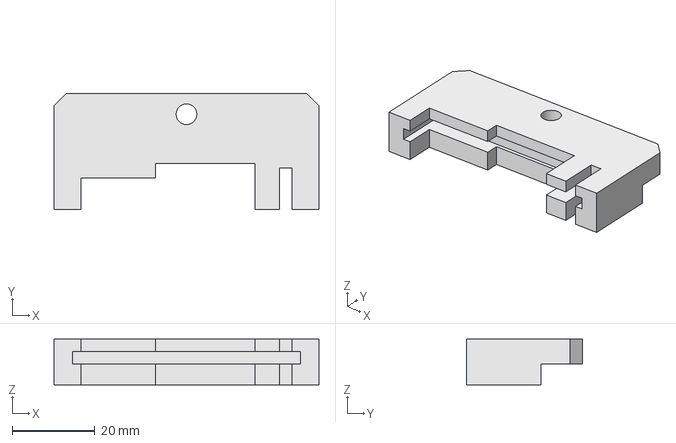
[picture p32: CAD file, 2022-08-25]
Source/CAD files/Freecad files/Arduino Holder/ELEC_P-Ard_G.FCStd
64.0 x 28.0 x 11.0 mm

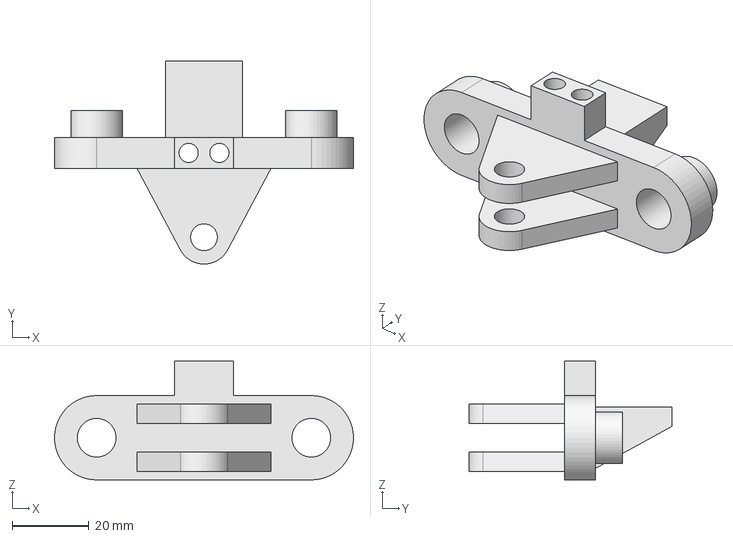
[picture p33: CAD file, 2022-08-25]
Source/CAD files/Freecad files/BladeHolder/Blade holder.FCStd
78.0 x 53.0 x 31.0 mm

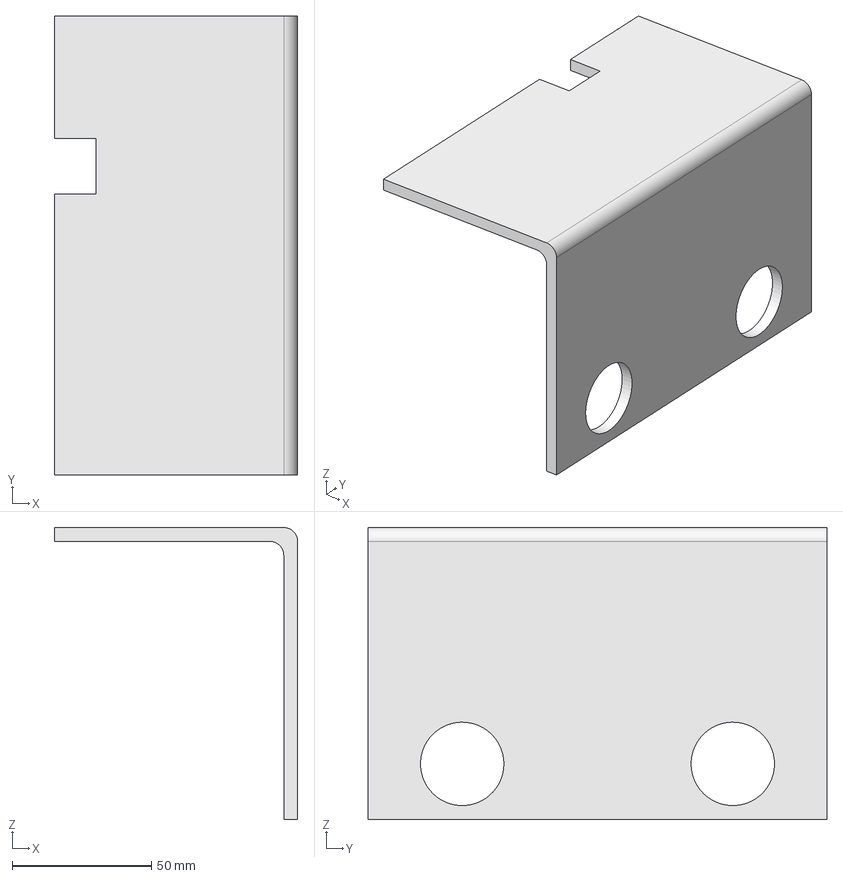
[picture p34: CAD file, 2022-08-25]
Source/CAD files/Freecad files/Box/STRUCT_Couv.FCStd
87.5 x 165.0 x 105.0 mm

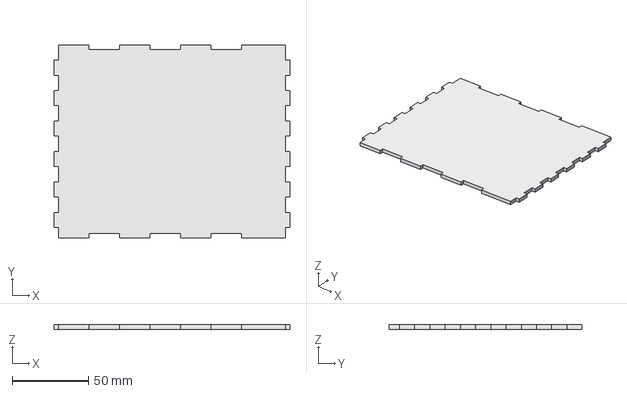
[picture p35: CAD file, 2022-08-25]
Source/CAD files/Freecad files/Drawer/STRUCT_T_B.FCStd
155.0 x 127.0 x 3.00 mm

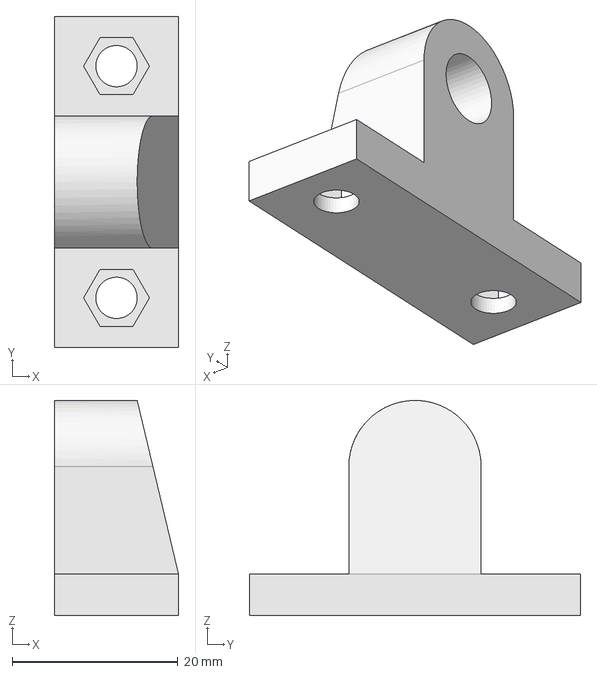
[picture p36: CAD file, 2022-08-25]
Source/CAD files/Freecad files/Guide Stop/PUISS_Guid_But.FCStd
15.0 x 40.0 x 26.0 mm

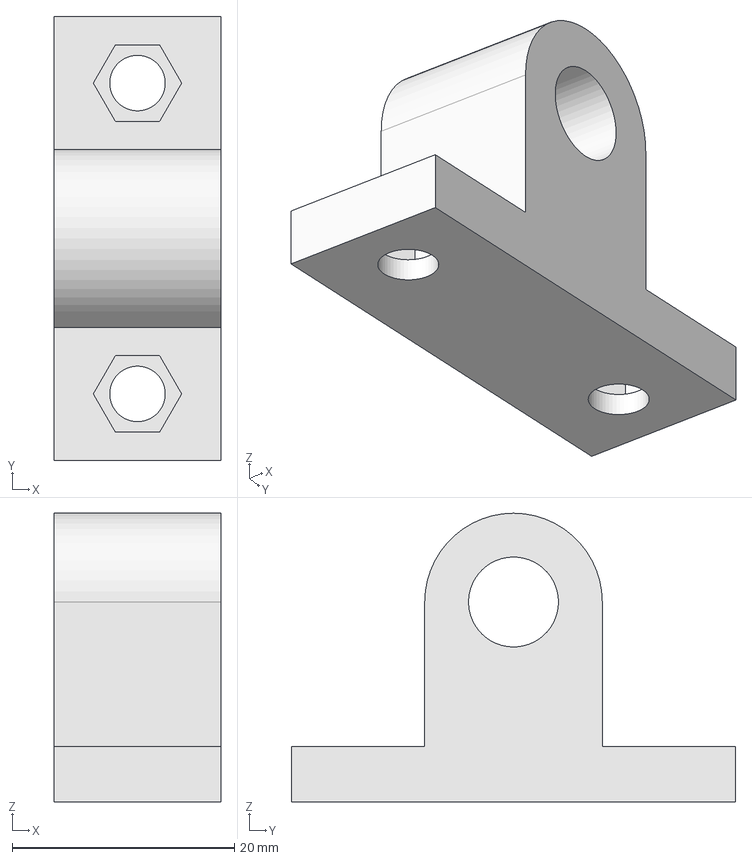
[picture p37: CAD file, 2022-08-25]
Source/CAD files/Freecad files/Guide Support/PUISS_Guid_Sup.FCStd
15.0 x 40.0 x 26.0 mm

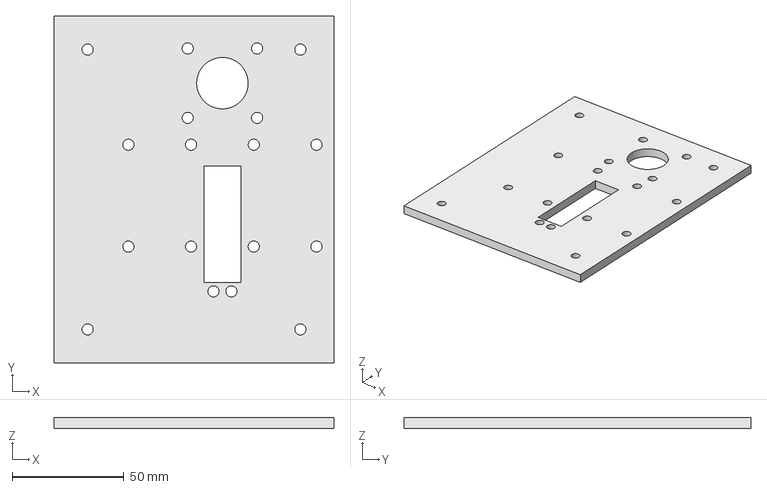
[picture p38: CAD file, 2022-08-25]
Source/CAD files/Freecad files/Motor support plate/STRUCT_Pl_Puiss.FCStd
125.0 x 155.0 x 5.00 mm

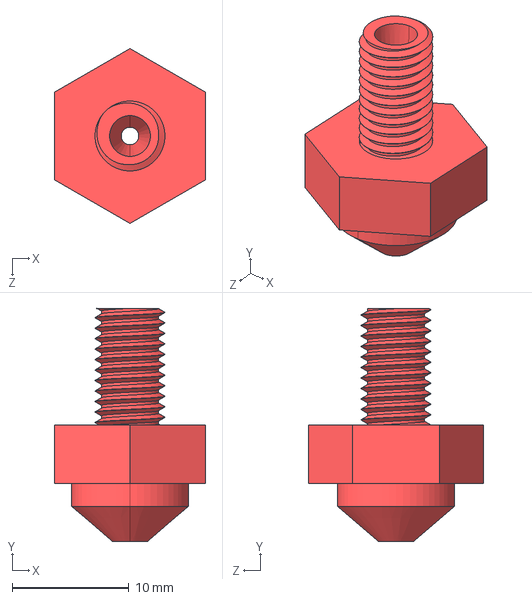
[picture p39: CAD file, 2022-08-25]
Source/CAD files/Freecad files/Nozzle/Nozzle(PUISS_Buse).STEP
13.0 x 20.0 x 15.0 mm

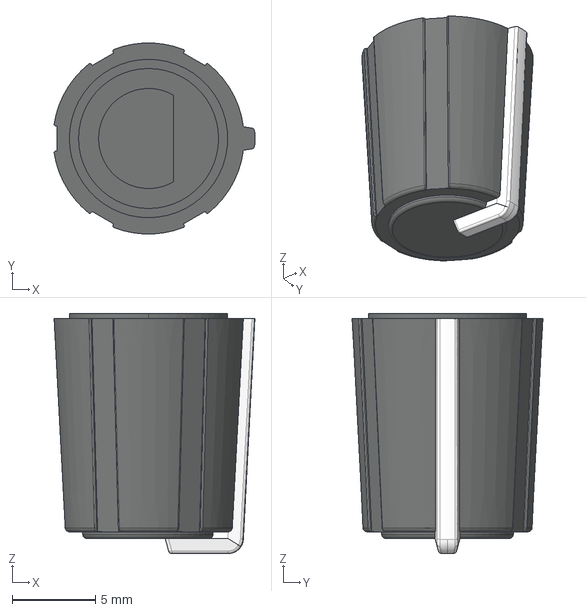
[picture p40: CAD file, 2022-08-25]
Source/CAD files/Freecad files/Potentiometer Button/ELEC_Bout-Pot.stp
12.1 x 11.5 x 14.4 mm

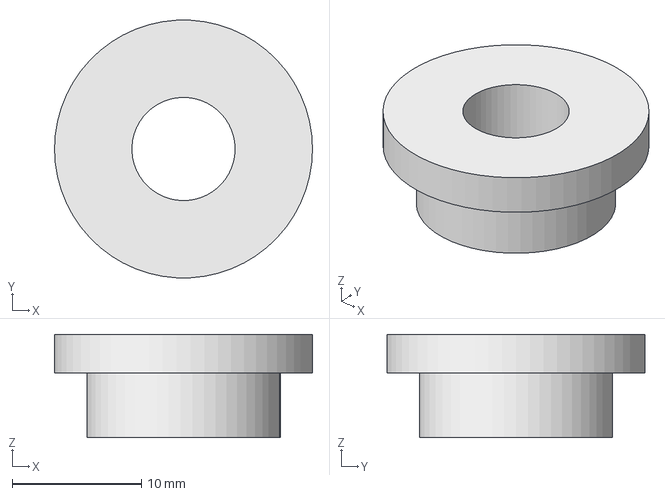
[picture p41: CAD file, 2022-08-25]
Source/CAD files/Freecad files/Potentiometer Holder/ELEC_P-Pot.FCStd
20.0 x 20.0 x 8.00 mm

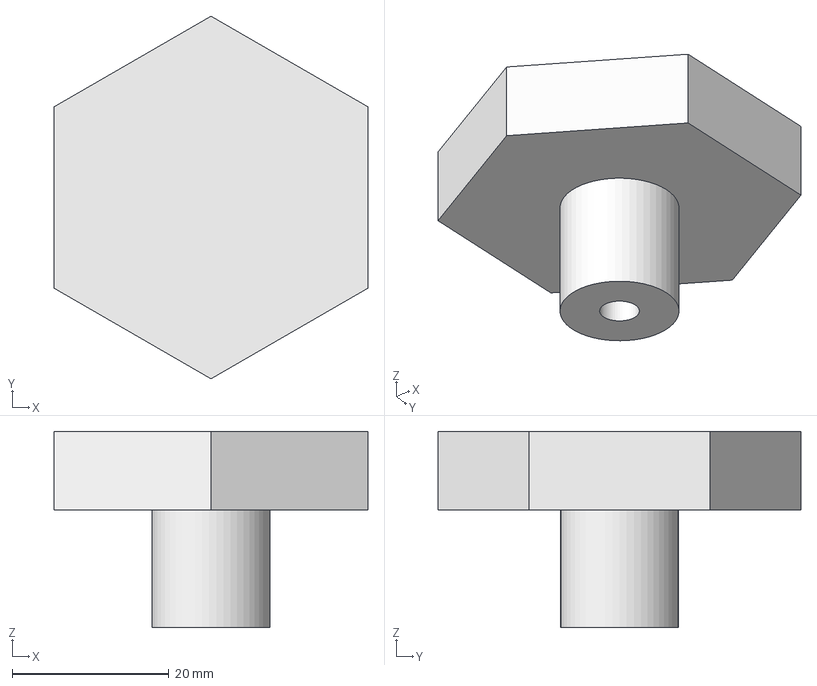
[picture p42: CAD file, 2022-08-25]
Source/CAD files/Freecad files/Threaded rod protection/STRUCT_Bob_Protect-TF.FCStd
40.0 x 46.2 x 25.0 mm

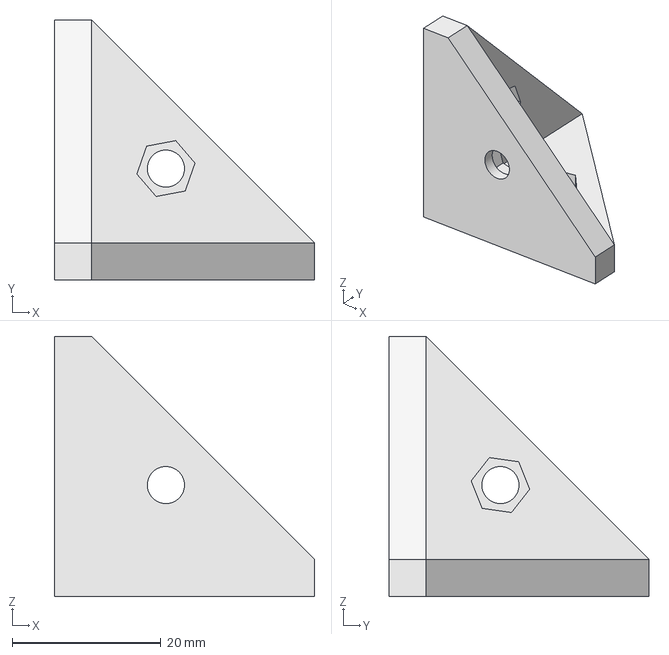
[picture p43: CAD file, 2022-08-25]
Source/CAD files/Freecad files/TrySquare/STRUCT_Eq.FCStd
35.0 x 35.0 x 35.0 mm

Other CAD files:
Source/CAD files/Freecad files/Wire positioning piece/STRUCT_Bob_Pos.FCStd
Source/CAD files/Ready to cut?(.Dxf file format)/Top plate.DXF
Source/CAD files/Ready to print?(.stl file format)/Nozzle - Nozzle(PUISS_Buse) (1).stl
Source/CAD files/SolidWorks files/Technical drawing/Came usiné.STEP
Source/CAD files/Freecad files/Air diverter for drivers/Air diverter for drivers.STEP
Source/CAD files/Freecad files/Arduino Holder/ELEC_P-Ard_D.FCStd
Source/CAD files/Freecad files/Arduino Holder/Left Arduino Holder(ELEC_P-Ard_G).STL
Source/CAD files/Freecad files/Arduino Holder/RightArduinoHolder(ELEC_P-Ard_D).STL
Source/CAD files/Freecad files/BladeHolder/Blade holder(PUISS_L_P-L).STL
Source/CAD files/Freecad files/Box/STRUCT_Pl_AR.FCStd
Source/CAD files/Freecad files/Box/STRUCT_Pl_AV.FCStd
Source/CAD files/Freecad files/Box/STRUCT_Pl_B.FCStd
Source/CAD files/Freecad files/Box/STRUCT_Pl_D.FCStd
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

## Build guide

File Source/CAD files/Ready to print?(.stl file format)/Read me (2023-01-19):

This repository contains all the STL files ready to print.

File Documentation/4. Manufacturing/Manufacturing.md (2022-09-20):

# Manufacturing

## 1. Bill of Materials

 - **Definition:** *A bill of materials (BOM) is a comprehensive list of parts, items, and other materials required to create a product, as well as instructions required for gathering and using the required materials.*

Component name |	Nomenclature |	Number of components |	Material |	Manufacturing technique |	Machine reference |	Manufacturing parameters |	Component reference |	Link |	Unit price
|:---:|:---:|:---:|:---:|:---:|:---:|:---:|:---:|:---:|:---:|
Structure	|
Plates |	
Back plate |	STRUCT_Pl_AR |	1 |	MDF  	| Découpe laser / Stratoconception					
Right plate	| STRUCT_Pl_D |	1		|					
Left plate	| STRUCT_Pl_G	| 1		|					
Inner plate	| STRUCT_Pl_M	| 1		|					
Front plate |	STRUCT_Pl_AV |	1	|						
Bottom plate |	STRUCT_Pl_B	| 1		|					
Top plate |	STRUCT_Pl_H |	1		|					
Motor support plate |	STRUCT_Pl_Puiss	| 1	|
Cover	| STRUCT_Couv |	1	| Plexiglass	| Découpe laser + plieuse |	Epilog laser fusion	|		
High magnet holder plate	| STRUCT_Pl_P-Aim_H |	2			|				
Front magnet holder plate	| STRUCT_Pl_P-Aim_AV	|							
Drawer		|							
Bottom plate |	STRUCT_T_B|	1	| Plexiglass |	Découpe laser	| Epilog laser fusion |
Front plate	| STRUCT_T_AV |	1			|
Rear plate|	STRUCT_T_AR	|1							
Left side plate	|STRUCT_T_G|	2							
Right side plate	|STRUCT_T_D								
Equerres									
Top front drawer (interface)	|STRUCT_Eq_Interf_H_AV|	8	|ABS|	Impression 3D	|Zortrax M200 				
Top back drawer (interface)|	STRUCT_Eq_Interf_H_AR								
Bottom front drawer (interface)|	STRUCT_Eq_Interf_B_AV								
Bottom back drawer (interface)	|STRUCT_Eq_Interf_B_AR								
Right front drawer (engine section)|	STRUCT_Eq_Puiss_D_AV								
Right back drawer (engine section)	|STRUCT_Eq_Puiss_D_AR								
Left front drawer (engine section)	|STRUCT_Eq_Puiss_G_AV								
Left back drawer (engine section) |	STRUCT_Eq_Puiss_G_AR								
Coil									
Coil	|STRUCT_Bob|	1	|Plastic						
Coil threaded rod	|STRUCT_Bob_TF	|1	|Steel	|	| |	|	M5 * 130		
Threaded rod protection	|STRUCT_Bob_Protect-TF|	1|	ABS	|Impression 3D	|Zortrax M200				
Wire positioning piece|	STRUCT_Bob_Pos|	1							
Magnet									
High-high magnet|	STRUCT_Aim_H_H	|4							
High-back magnet	|STRUCT_Aim_H_B								
Front-front magnet|	STRUCT_Aim_AV_AV								
Back-back Magnet	|STRUCT_Aim_AV_AR								
Engine section									
Engine									
Stepper motor 1 (M1)|	PUISS_Mot_Extr	|1		|	|	| |	|		Moteur pas à pas Joy-it SM42HT38-1684A NEMA-17-01 0.4 Nm 1.68 A Diamètre de l'arbre: 5 mm 1 pc(s) |	https://www.conrad.fr/p/moteur-pas-a-pas-joy-it-nema-17-01-04-nm-168-a-diametre-de-larbre-5-mm-1-pcs-1597325	31,99
Stepper motor 2 (M2)	|PUISS_Mot_Cam	|1		|	|	| |	|		Joy-it Moteur pas à pas NEMA17-06 0.59 Nm 2 A 2 A Diamètre de l'arbre: 5 mm|	https://www.conrad.fr/p/joy-it-moteur-pas-a-pas-nema17-06-059-nm-2-a-2-a-diametre-de-larbre-5-mm-2355876	21,49
Extruder	|PUISS_Extr	|1			|	 |	| |	|	Extrudeur aluminium MK8 direct drive montage droit ou gauche |imprimante-3d-service.com
Nozzle	|PUISS_Buse|	1	|ABS|	Impression 3D	|Zortrax M200 plus|	impression haute qualité, épaisseur la plus finne possible, sortie de fil vers en haute			
Bearing	|Puiss_RaB_Extr	|1		| | | | |			625ZZ		
Cam	|PUISS_Cam|	1|	Aluminium|	Tournage					
Guide									
Front guide stop	|PUISS_Guid_But_AV|	2	|ABS|	Impression 3D	|Zortrax M200 				
Back guide stop	|PUISS_Guid_But_AR								
Front guide support	|PUISS_Guid_Sup_AV|	2							
Back guide support	|PUISS_Guid_Sup_AR								
Front guide rod	|PUISS_Guid_Tige_AV	|2	|Aluminium	|Scie à métaux					
Back guide rod	|PUISS_Guid_Tige_AR								
Ball bearing	|PUISS_Guid_RaB|	1	| | | | |				608ZZ		
Back spring guide|	PUISS_Guid_Ress_AR|	2	|Acier						
Front spring guide	|PUISS_Guid_Ress_AV								
Blades									
Moving blade	|PUISS_L_Mob	|2|	Acier	| | | | 				Lame de dénudage pour machine à dénuder à fil SWT508 | AliExpress	
Stationary blade|	PUISS_L_Immob								
Blade holder	|PUISS_L_P-L|	1	|ABS	|Impression 3D|	Zortrax M200 				
Blade support spring	|PUISS_L_Ress|	1	|Acier						
Electronics									
Supports									
Test plate|	ELEC_Pl-Essai|	1							
Left arduino holder	|ELEC_P-Ard_G|	2	|ABS	|Impression 3D	|Zortrax M200 				
Right arduino holder|	ELEC_P-Ard_D								
Driver holder	|ELEC_P-Driv	|1							
Top potentiometer holder	|ELEC_P-Pot_H	|2							
Bottom potentiometer holder|	ELEC_P-Pot_B
Potentiometer button connector | ELEC_Bout_Pot_Connect | 1 | Plexiglass|	Découpe laser | Epilog laser fusion
Coaxial cable end holder | ELEC_P-Alim | 1 | Impression 3D |	Zortrax M200
Accessories									
Top potentiometer button|	ELEC_Bout-Pot_H	|2|	ABS	|Impression 3D	|Zortrax M200 				
Bottom potentiometer button	|ELEC_Bout-Pot_B								
Green push button	|ELEC_Bout_V|	1							
Push button yellow	|ELEC_Bout_J	|1							
Push button red	|ELEC_Bout_R|	1							
Green push button holder	|ELEC_Supp-Bout_V	|3							
Yellow push button holder	|ELEC_Supp-Bout_J								
Red push button holder	|ELEC_Supp-Bout_R								
Air diverter for drivers	|ELEC_Dir-air|	1	|ABS|	Impression 3D	|Zortrax M200 				
Components									
Driver 1 (D1)	|ELEC_Driv_Extr	|2	| | | | |				TB6612FNG Dual Motor Driver Carrier	|https://www.pololu.com/product/713|	9,95
Driver 2 (D2)	|ELEC_Driv_Cam								
Driver 1 radiator	|ELEC_Rad_Driv_Extr|	2		|	| | | |		 Résistance thermique:123°C/W; Boîtiers refroidis:SOIC-8, SOIC-14, SSOP-16, TSSOP-14, TSSOP-16; Largeur externe - Métrique:6.3mm; Hauteur externe - Métrique:4.8mm; Longueur externe -| 	https://fr.farnell.com/webapp/wcs/stores/servlet/CompareProductsDisplay?catalogId=15001&langId=-2&storeId=10160&catentryId=64708491&pageType=PDP	|0,618
Driver 2 radiator	|ELEC_Rad_Driv_Cam								
Capacitor (C)|	ELEC_Cond|	1		|	| | | |		Capacitor 47μF, 16V c.c.|	https://fr.rs-online.com/web/p/condensateurs-electrolytiques/7110927?cm_mmc=FR-PLA-DS3A-_-google-_-CSS_FR_FR_Passifs_Whoop-_-(FR:Whoop!)+Condensateurs+%C3%A9lectrolytiques-_-7110927&matchtype=&pla-339621668050&gclid=Cj0KCQjwxIOXBhCrARIsAL1QFCaT7Q_rE7X_4SQt8N8Zu6aHp6PKWwv3yTqLVZFDtoSgLZNFndHlv44aApaUEALw_wcB&gclsrc=aw.ds	|0,078
Pushbutton 1 (B1)	|ELEC_Bout_V	|1|	| | | |				Bouton-poussoir, NO, Montage panneau|	https://fr.rs-online.com/web/p/boutons-poussoirs/8151834?aud-871567053779%3Apla-365975203081&cm_mmc=FR-PLA-DS3A-_-google-_-CFS_FR_FR_Schneider_Whoop-_-(FR%3AWhoop!)%20Interrupteurs%20(2)-_-8151834&gclid=Cj0KCQjwxIOXBhCrARIsAL1QFCZbOdo6Ri0mEeT1leJcbMdhEjlsmj2F4bzqcQj8dS_wv5ovp86AldUaAt9hEALw_wcB&gclsrc=aw.ds&matchtype=	|16,9
Pushbutton 2 (B2)	|ELEC_Bout_J|	1	|		| | | | | |				16,9
Pushbutton 3 (B3)	|ELEC_Bout_R|	1	|		| | | | | |								16,9
Potentiometer 1 (P1)	|ELEC_Pot_H|	2		|	| | | |				Potentiometer: Resistance 10kohm, 1 turn, Linear, 500mW, resistance tolerance ± 20%	|https://fr.farnell.com/tt-electronics-bi-technologies/p231-fc20br10k/potentiometre-rotatif-10k-20mm/dp/2771755?st=potentiometre%20rotatif	|1,68
Potentiometer 2 (P2)	|ELEC_Pot_B								
Green LED 1 (L1)|	ELEC_LED_1	|4			|	| | | |			LED Vert, Traversant, 5 mm (T-1 3/4), 2 V	|https://fr.rs-online.com/web/p/leds/7088022p?cm_mmc=FR-PLA-DS3A-_-google-_-CSS_FR_FR_Afficheurs_et_optoelectronique_Whoop-_-(FR:Whoop!)+LEDs-_-7088022P&matchtype=&pla-834413916684&gclid=Cj0KCQjwxIOXBhCrARIsAL1QFCYk1e3LMUt7p1XBNJRN2BUuUm2WMwk3iOHTFCnizzsr4hlkoqhmzT8aAi9eEALw_wcB&gclsrc=aw.ds	|0,268
Green LED 2 (L2)|	ELEC_LED_2								
Green LED 3 (L3)|	ELEC_LED_3								
Green LED 4 (L4)|	ELEC_LED_4								
Red LED 5 (L5)|	ELEC_LED_5|	1			|	| | | |			LED Rouge, Traversant, 5 mm (T-1 3/4), 2,6 V	|https://fr.rs-online.com/web/p/leds/1278393?cm_mmc=FR-PLA-DS3A-_-google-_-CSS_FR_FR_Afficheurs_et_optoelectronique_Whoop-_-(FR:Whoop!)+LEDs-_-1278393&matchtype=&pla-302722872933&gclid=Cj0KCQjwxIOXBhCrARIsAL1QFCYVfGLEzypoiNEvZWrra4NUpec1AlHI-cAAueNsmEW-s_PTFDmVd0UaAoqTEALw_wcB&gclsrc=aw.ds	|0,088
Resistance 1 (R1)|	ELEC_Resist_Bout_V	|8	|	| | | |					Résistance Film carbone 100Ω ±5%, 0.25W	|https://fr.rs-online.com/web/p/resistances-traversantes/7077587	|0,278
Resistance 2 (R2)	|ELEC_Resist_Bout_J								
Resistance 3 (R3)|	ELEC_Resist_Bout_R								
Resistance 4 (R4)|	ELEC_Resist_LED_1								
Resistance 5 (R5)	|ELEC_Resist_LED_2								
Resistance 6 (R6)	|ELEC_Resist_LED_3								
Resistance 7 (R7)|	ELEC_Resist_LED_4								
Resistance 8 (R8)|	ELEC_Resist_LED_5	
5V power supply	|ELEC_Alim5V	|1	|	| | | |					Alimentation AC/DC, ITE, 1 sortie, 2.75 W, 5 V, 550 mA	|https://fr.farnell.com/brainboxes/pw-600/power-supply-5v-1a-es-357/dp/2096366?st=alimentation%205v	|27,77
12V power supply|	ELEC_Alim12V	|1		|	| | | |				Adaptateur AC/DC 12V c.c., 2A, 24W, , Régulée	|https://fr.rs-online.com/web/p/adaptateurs-ac-dc/1753324?cm_mmc=FR-PLA-DS3A-_-google-_-CSS_FR_FR_Alimentations_et_transformateurs_Whoop-_-(FR:Whoop!)+Adaptateurs+AC/DC-_-1753324&matchtype=&pla-370976687757&gclid=Cj0KCQjwxIOXBhCrARIsAL1QFCbjgBdOY3BMhupPiywYVdsT5aeT05L4zefR6RXDtFUW6gS1CuGbczEaAmj8EALw_wcB&gclsrc=aw.ds	|16,26
5V coaxial cable end	|ELEC_Embout_5V	|2	|	| | | |					Prise d'alimentation CC, 5A, Montage sur CI, 12 V c.c.	|https://fr.rs-online.com/web/p/connecteurs-d-alimentation-dc/8051696|	2,359
12V coaxial cable end	|ELEC_Embout_12V								
Ventilator 1|	ELEC_Ventilo_Mot|	2				|	| | | |			Ventilateur axial RS PRO 5 V c.c., 11.9m³/h, 40 x 40 x 10mm, 1.92W|	https://fr.rs-online.com/web/p/ventilateurs-axiaux/7897858?cm_mmc=FR-PLA-DS3A-_-google-_-CSS_FR_FR_Chauffage_%26_ventilation_et_air_conditionne_Whoop-_-(FR:Whoop!)+Ventilateurs+axiaux+(2)-_-7897858&matchtype=&pla-475514636566&gclid=Cj0KCQjwxIOXBhCrARIsAL1QFCZHMrid9mmDNu3gS1Z1DK1VgvmU1g3jfntRcnVzLYc1X8ZK7yz8A9QaAoOXEALw_wcB&gclsrc=aw.ds	|7,08
Ventilator 2|	ELEC_Ventilo_Driv								
Arduino card|	ELEC_Ard	|1			|	| | | |				UNO Rév. 3 Arduino|	https://fr.rs-online.com/web/p/arduino/7154081?cm_mmc=FR-PLA-DS3A-_-google-_-CSS_FR_FR_Raspberry_Pi_%26_Arduino_%26_Outils_de_developpement_Whoop-_-(FR:Whoop!)+Arduino-_-7154081&matchtype=&aud-827186183686:pla-339391921421&gclid=Cj0KCQjwxIOXBhCrARIsAL1QFCZg_iLNqiF-tBPj6V5rdmA0EW2CjRNORrWGV6KyqY_00fqD72AHXBQaArdnEALw_wcB&gclsrc=aw.ds	|28,1
Other									
Wire	|ELEC_Fils|	x							
Heat shrinkable tubing	|ELEC_Gaines|	x							
Wire end cap male	|ELEC_Embout_fil_M	|x							
Female wire end	|ELEC_Embout_fil_F|	x							
Soldering

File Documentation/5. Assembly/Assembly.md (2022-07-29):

# Assembly

## Assembly instructions

- **Definition:** *Assembly instructions could illustrate visually and with words and text how to assemble or disassemble the mechanical and electrical components of the product.*

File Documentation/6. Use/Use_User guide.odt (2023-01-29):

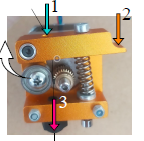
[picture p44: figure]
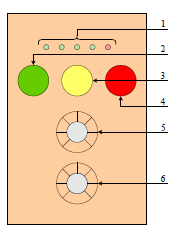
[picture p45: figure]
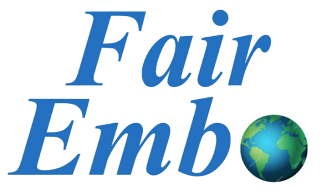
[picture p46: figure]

Instructions for Wire-Cutting machine

Set up of the wire in the extruder | Set up: Place the spool in the position provided and then pass the wire through the black component on top of the device. Remove the plastic cover of the machine and put the wire in the hole at the end of the arrow 1. Press the lever (arrow 2) to separate the gear from the bearing. Keep pressing the lever, make sure the wire pass through between 2 wheels and then through the nozzle (arrow 3) Close the cover and select the required cut particle size (5) and the length of wire remained in the spool (6) on the user interface

User interface of the machine

User interface controls

1. Progress of the cutting program
2. Start button
3. Pause button
4. Stop button
5. Particle’s length
6. Spool’s length

How to use the machine?

A. To start the program, press the Start button (2), the entire wire of the coil will be cut.
B. For any reason, if the user wants to pause the program, press the Pause button(3). To restart the device, press the Start button (2) again.
C. To stop the program completely and reset the positioning, press the Stop button (4).
D. The progress of the cutting program is indicated by the LED (1) on top. (Each LED represents to 20% of the progress). When the end of the LED is on, it means that the cutting program is done.

Notice:

1. The buttons are not very sensible, make sure to remain pressing the button for a couple of seconds.
2. When a cutting program finish and changing to the other particle’s length and spool length, make sure to press the Stop button (4) to initialize the program first.

| Don’t start the machine if the cover is not closed. Don’t open the cover if the machine is running Be careful to plug the power supply.

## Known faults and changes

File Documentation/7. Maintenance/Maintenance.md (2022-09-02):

# Maintenance

  - **Definition:** *A maintenance instruction is a technical communication document intended to give recommendations and necessary information to maintain the system effectively.*
 
 ## 1. Identifying the defective components 

<p align="center">
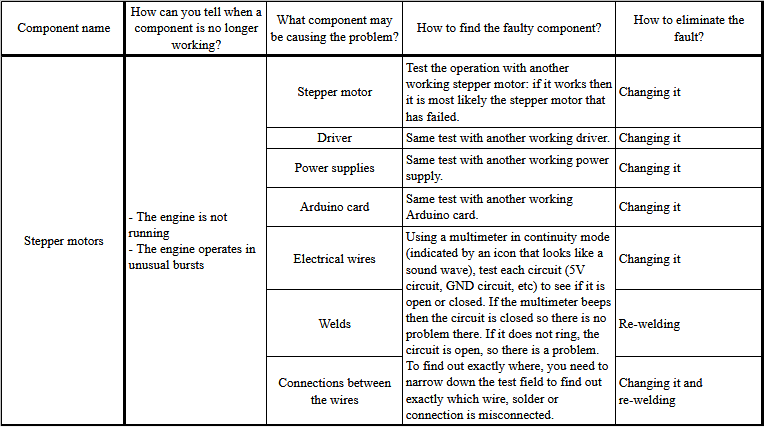
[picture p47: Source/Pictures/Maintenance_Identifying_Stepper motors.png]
  
<p/>
<p align="center">
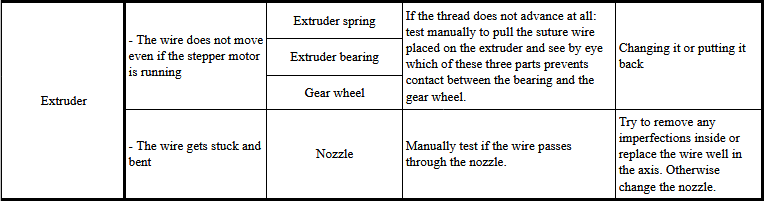
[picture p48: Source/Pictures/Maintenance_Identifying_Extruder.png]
  
<p/>
<p align="center">
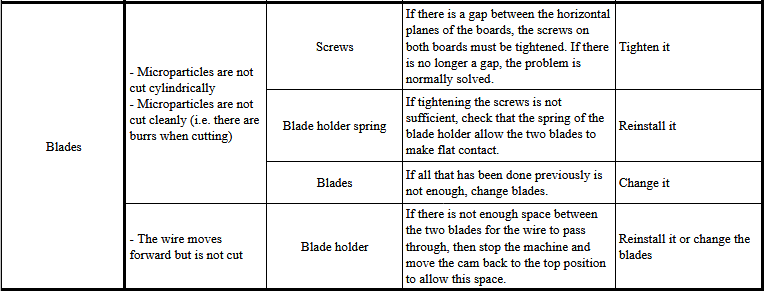
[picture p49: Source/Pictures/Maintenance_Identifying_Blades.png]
  
<p/>
<p align="center">
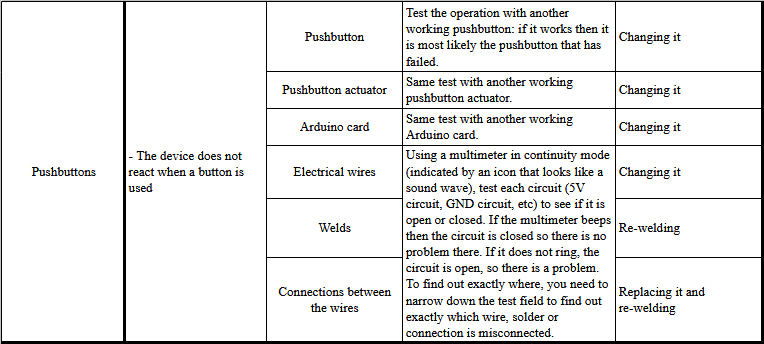
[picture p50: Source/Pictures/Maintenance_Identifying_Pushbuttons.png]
  
<p/>
<p align="center">
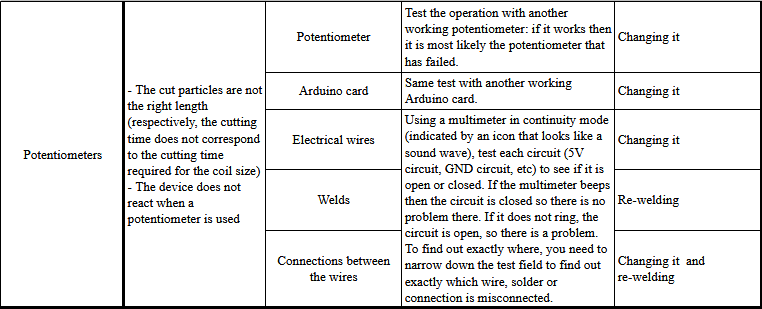
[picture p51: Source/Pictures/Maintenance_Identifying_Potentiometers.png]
  
<p/>
<p align="center">
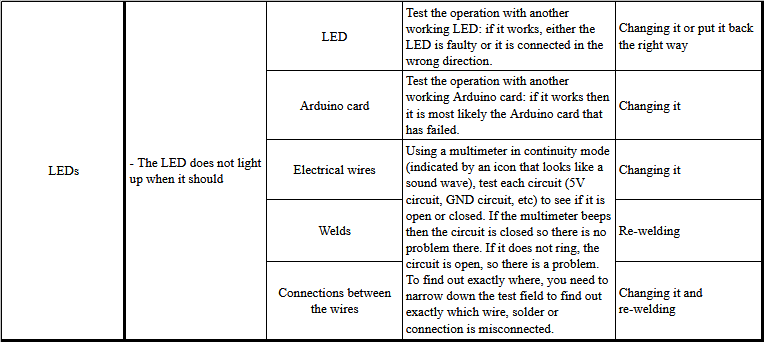
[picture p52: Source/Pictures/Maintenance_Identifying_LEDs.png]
  
<p/>
<p align="center">
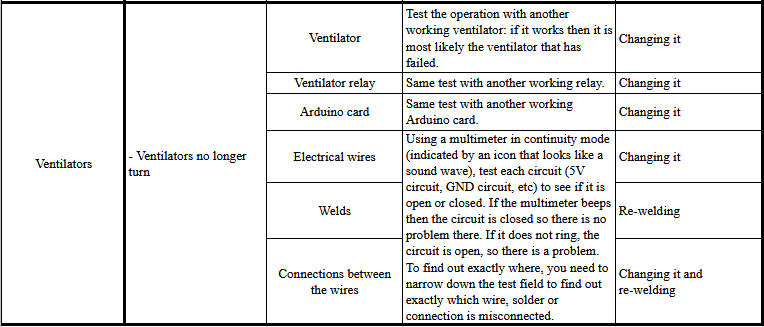
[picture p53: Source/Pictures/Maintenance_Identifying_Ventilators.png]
  
<p/>

 ## 2. Replacing equipment components on a schedule
 
image of replacing components

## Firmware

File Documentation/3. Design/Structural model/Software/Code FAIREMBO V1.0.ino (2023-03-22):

//PROJET FAIREMBO code V2.0

//LIANG CHAOJI  x  GOSNIK TOM

//=======================================================================================//

//PINS 

//STEPMOTORS
#define DirWire 5
#define StepWire 4
#define DirCam 3
#define StepCam 2

#include <Stepper.h>

Stepper WireMotor( 3200, DirWire, StepWire );
Stepper CamMotor( 200, DirCam, StepCam );

//BUTTONS
#define StartButton 13
#define BreakButton 11
#define StopButton 12
#define RelayDriver A2 


//LEDS
#define led1 10
#define led2 9
#define led3 8
#define led4 7
#define led5 6

//=========================================================================================//

//VARIABLES :

int Speed = 1000;           // Vitesse de rotation des moteurs
int Start = 0;             // Etat du système (à 0 pour dire qu'il n'est pas démarré)
int radiusExtruder = 5.5;  // Rayon de l'extrudeur en mm
int ParticlesLength = 0;   // Longueur des particules à découper
int Step = 0;              // Nombre de pas à faire par le moteur guidant le fil
int Max = 0;               // Nombre maximum de particules à découper par bobine
int ParticlesNumber = 0;   // Nombre de particules découpées en temps réel

//=========================================================================================//

//SETUP :

void setup() {

  //SERIAL
  Serial.begin( 9600 );
  
  //BUTTONS
  pinMode( StartButton, INPUT );
  digitalWrite( StartButton, LOW );
  pinMode( BreakButton, INPUT );
  digitalWrite( BreakButton, LOW );
  pinMode( StopButton, INPUT );
  digitalWrite( StopButton, HIGH );

  
  //STEPMOTORS
  CamMotor.setSpeed( Speed );
  WireMotor.setSpeed( Speed );

  //LEDS
  pinMode( led1, OUTPUT );
  digitalWrite( led1, LOW );
  pinMode( led2, OUTPUT );
  digitalWrite( led2, LOW );
  pinMode( led3, OUTPUT );
  digitalWrite( led3, LOW );
  pinMode( led4, OUTPUT );
  digitalWrite( led4, LOW );
  pinMode( led5, OUTPUT );
  digitalWrite( led5, LOW );
  //Relay 
  pinMode( RelayDriver,OUTPUT);
  digitalWrite( RelayDriver, LOW);

}

//=========================================================================================//

//LOOP :

void loop() {
  //Si on appuie sur le bouton Start on lance le programme (bouton est normalement ouvert)
  
  //Serial.println(Start);
  if( digitalRead( StartButton ) == HIGH ){ 
    //Le relais envoie un signal à ventilo 
    digitalWrite( RelayDriver, HIGH );
    delay(100) ;

    // Variables de départ    
    Start = 1;
    ParticlesNumber = 0;

    // Variables associées aux fonctions
    Step =  ( WireLength() / radiusExtruder ) * ( 25600 / 6.28 );    // Nombre de pas à faire en fonction de la taille du fil à découper
    //25600 est le nombre de pas un tour de moteur

    Max = round( CoilLength() / WireLength() );                        // Nombre de particules à découper en fonction de la bobine

    // LEDs éteintes
    digitalWrite( led1, LOW );
    digitalWrite( led2, LOW );
    digitalWrite( led3, LOW );
    digitalWrite( led4, LOW );
    digitalWrite( led5, LOW );

  }
  
  while( Start == 1 ){
    //Le relais envoie un signal à ventilo 
    // Le moteur de l'extrudeur tourne puis le moteur de la came fait un tour
    //Serial.println(Step);
    WireMotor.step( Step );
    delay( 2 );
    CamMotor.step( 800 ); //25600
    delay( 200 );

    // Compteur de particules coupées
    ParticlesNumber = ParticlesNumber + 1;
    
    // Si on appuie sur le bouton Pause on arrête le système (boutons normalement ouvert)
    if( digitalRead( BreakButton ) == HIGH ) {
     //Le relais envoie un signal à ventilo 
     digitalWrite( RelayDriver,HIGH );
      // Tant qu'on n'appuie ni sur le bouton Start ni sur le bouton Stop (boutons normalement fermé), le système est en pause
      while( digitalRead( StartButton ) == LOW and Start == 1 ) {
      delay(100) ;

        // Si on appuie sur le bouton Stop, le système s'arrête totalement
        if( digitalRead( StopButton ) == LOW ) {  
        //Le relais envoie un signal à ventilo 
        digitalWrite( RelayDriver, LOW);
      
          Start = 0;
          delay( 50 );
        
        }
        
        delay( 50 );
        
      }
      
    }

    // Si on appuie sur le bouton Stop on arrête le système
    if( digitalRead( StopButton ) == LOW ) {
     //Le relais envoie un signal à ventilo 
      digitalWrite( RelayDriver, LOW);
      


      Start = 0;
      delay(100) ;  
    }
      

    //Si la bobine est utilisée au 1/5 
    if( ParticlesNumber == round( Max / 5 ) ) {

      digitalWrite( led1, HIGH );
      
    }

    //Si la bobine est utilisée aux 2/5 
    if( ParticlesNumber == round( ( Max * 2 ) / 5 ) ) {

      digitalWrite( led2, HIGH );
      
    }
    
    //Si la bobine est utilisée aux 3/5 
    if( ParticlesNumber == round( ( Max * 3 ) / 5 ) ) {

      digitalWrite( led3, HIGH );
      
    }

    //Si la bobine est utilisée aux 4/5 
    if( ParticlesNumber == round( ( Max * 4 ) / 5 ) ) {

      digitalWrite( led4, HIGH );
      
    }

    // Si la bobine est épuisée on arrête le système 
    if( ParticlesNumber >= Max ) {

      digitalWrite( led5, HIGH );
      Start = 0;
      delay(5000);
        
      }
    
  }
  
  delay(20);

  // On éteint tout 
  digitalWrite( led1, LOW );
  digitalWrite( led2, LOW );
  digitalWrite( led3, LOW );
  digitalWrite( led4, LOW );
  digitalWrite( led5, LOW );
  digitalWrite( RelayDriver, LOW);
  
}

//=========================================================================================//

// FONCTION SELECTION TAILLE DE FIL
// Retourne la taille du fil à couper en fonction de l'information donné par le potentiomètre

float WireLength(){
  
  float CuttingLength;
  
  
  int pot0 = analogRead( A0 );  // lis la valeur du potentiometre
  Serial.println(pot0);
  
  if( pot0 <= 150 ){
    CuttingLength = 0.3;
  }
  
  if( 150 < pot0 and pot0 <= 400 ){
    CuttingLength = 0.5;
  }  
  
  if( 400 < pot0 and pot0 <= 650 ){
    CuttingLength = 0.7;
  }  
  
  if( 650 < pot0 and pot0 <= 900 ){
    CuttingLength = 0.9;
  }  
  
  if( 900 < pot0 ){
    CuttingLength = 1.1;
  }
  //Serial.print(",");  
  //Serial.println(CuttingLength);
  return( CuttingLength ); 

}

// FONCTION SELECTION LONGUEUR DE LA BOBINE

int CoilLength() {
  
  float Length;
  
  int pot1 = analogRead( A1 );
  
  if( pot1 <= 150 ){
    Length = 500;
  }
  
  if( 150 < pot1 and pot1 <= 400 ){
    Length = 1000;
  }  
  
  if( 400 < pot1 and pot1 <= 650 ){
    Length = 2000;
  }  
  
  if( 650 < pot1 and pot1 <= 900 ){
    Length = 3000;
  }  
  
  if( 900 < pot1  ){
    Length = 5000;
  }
  
  Serial.print("\t"); 
  Serial.println(pot1);
  return( Length );
  
}

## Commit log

2022-07-25 Create Assembly
2023-06-07 Rename Stage-code-07.ino to Code FAIREMBO V1.0.ino
